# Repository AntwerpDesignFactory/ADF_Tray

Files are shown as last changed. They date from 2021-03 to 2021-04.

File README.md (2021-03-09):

# Vaccine preparation tray

## The problem
The fight against the Covid-19 pandemic continues and countries are setting up vaccination strategies to protect their population. Many hospitals and vaccination centres worldwide are dealing with challenges of setting-up a fast, efficient, and safe vaccination plan.  

One of the challenges is the preparation of the vaccine syringes. Covid-19 vaccines are delivered in vials containing 6 to 11 doses, depending on the producer of the vaccine. Doses from the vial need to be drawn up into syringes, so that one syringe can be used to vaccinate one patient. 

To speed up the vaccination process, preparation of the vaccine syringes is done by the pharmacy and injection of the vaccine is done by a nurse or physician. This means that the vaccine syringes need to be transported from the pharmacy to the location where the vaccine is administered. It is also necessary to keep track of which vaccine (producer and lot number) every patient receives. That is why correct labelling of transported vaccines is particularly important.  

At the moment, hospitals and vaccination centres often use so-called ‘kidney dish’ to collect and transport syringes. Kidney dishes are used for various medical applications; however, this bowl is not always the best solution. Syringes are mixed up which makes it difficult to take out one, because of this, precious time is lost, and it can lead to administering errors. Healthcare organisations were looking for a better alternative to transport the vaccine syringes. 

## The design
IMAGE ALT TEXT (https://www.youtube.com/watch?v=rdpCua8XM-c "ADF - Vaccin tray design")

- It fits all syringes we so far have seen selected for COVID-19 vaccine applications. Ranging from 6 to 11 mm diameter and volumes of 1 to 2 ml.
- The Tray is designed to hold the syringes of one vial of Moderna vaccine (11 doses), one vial AstraZeneca vaccine (8 to 10 doses) and two vials of Pfizer vaccine (two times 6 doses).
- Trays are securely stackable, both filled with syringes and empty. Empty trays nest into each other, this way saving space. 
- The general dimensions of the tray are roughly an A4 in size and 2 cm tall. This size should fit most actively used fridges or trolleys conveniently. 
- On both sides is a flat surface foreseen to place a label of the specific vial brand, batch and details.
- The central surface of the tray can be used to place branding in the form of a logo or a sticker.

## The benefits
- Syringes nicely organized.
- Safe transportation.
- Easy to count and keep track of.
- Traceability from vial to patient.
- Quick check of volumes in each syringe.
- Re-usable by cleaning it with IPA or dish-washing it with soap.
- Securely stackable.
- Easy to take out syringes at the patients side. 
- Prevents from a accidently pushing in any plungers 

## Material choice:
### For the mould:
- We advise using high-temperature, high density polyurethane tooling foam for this application 
- Organizations with experience can use their materials of choice for the mould.
- MDF might also be suitable, but might break after a few uses since the design contains thin-high pieces. 
- 3D printing may also be a good choice. But SLA printer are preferred over FDM prints since the layer steps on FDM make the trays hard to clean.

### For the tray:
- PETG or Vivak is advised as a medical choice and provided a decent amount of stiffness. It can be vacuum formed well and can stand cleaning with IPA and soaps. 
    - A thickness of 1mm is advised to have a decent strength.
    - In PETG there are not many colour options. So clear PETG is the best option.
- PP would be the second best pick because of again its medical purpose. But is a lot harder to form well whilst vacuum forming. The material needs to be at the exact optimal temperature and often warps if not done perfect. 

## How to make it
The tray is designed to be vacuum formed out of 1mm PETG or PP. This means a mould must be made first to form the plastic sheet over.

1. The mould is milled out of a solid piece of this foam using a CNC mill.
1. The mould needs extra ventilation holes to allow air to be pulled out of the cavities. This is done with thin long drills of around a millimeter in diameter. In our mould we drilled about 50 holes in corners and deep parts.

1. The mould also needs lubrication to allow the plastic sheet to release with ease. We applied a thin coat of Vaseline, but silicone release sprays would work as well. This release agent does need to be cleaned off of the tray after forming before use.
1. In the design branding in the form of a 3D logo is left out since these small features might be hard to mill. Thus these can be added at this moment as thin 3D printed pieces.
Also two arrows are placed at this moment to help visualising what label fits with that side of the trays syringes in case the vial holds 6 doses or less.
1. Remove the protective foils from both sides of your plastic sheet.
1. Depending on your machine you first place the mould or place the sheet of plastic. But in general words prepare the machine and pre-heat the sheet of plastic.
1. As the sheet hits around 150°C (after about 30sec) it should be ready to be pulled over the mould. 
1. Let it cool down on the mould until the plastic has hardened again.
1. Take out of the machine and pull out the mould from the tray. Blowing in compressed air from the sides may help with the pop.
1. The tray is now left with a brim that can be cut off using a sharp blade, a bandsaw, a grinder of any other tool that you prefer. The cutting edge is foreseen as a flat rim that can be cut easily on the table.
1. Remove sharp edges with a file or sanding paper.
1. Clean the tray before use to remove the release agent and dust.

Check out more detailed guides online if more help is needed. For example this guide from [Formech](https://mhubchicago.com/media/148882/business/3625/PDI_Vacuum_forming_guide.pdf) is a good resource.

## Attribution
This tray is a design of the [Antwerp Design Factory](https://antwerpdesignfactory.be). 
A research group of the [department of product development](https://www.uantwerpen.be/nl/studeren/aanbod/alle-opleidingen/productontwikkeling-studeren/) at the [University of Antwerp](https://www.uantwerpen.be/nl/studeren/aanbod/alle-opleidingen/productontwikkeling-studeren/).

The design is released under a [Creative Commons Attribution Share Alike 4.0 International licence](LICENCE). So you are free to share and modify this design. May even use it for commercial use. But, are not allowed to patent the design and are required to attribute our work when sharing.

---

Shield: [][cc-by-sa]

This work is licensed under a
[Creative Commons Attribution-ShareAlike 4.0 International License][cc-by-sa].

[][cc-by-sa]

[cc-by-sa]: http://creativecommons.org/licenses/by-sa/4.0/
[cc-by-sa-image]: https://licensebuttons.net/l/by-sa/4.0/88x31.png
[cc-by-sa-shield]: https://img.shields.io/badge/License-CC%20BY--SA%204.0-lightgrey.svg

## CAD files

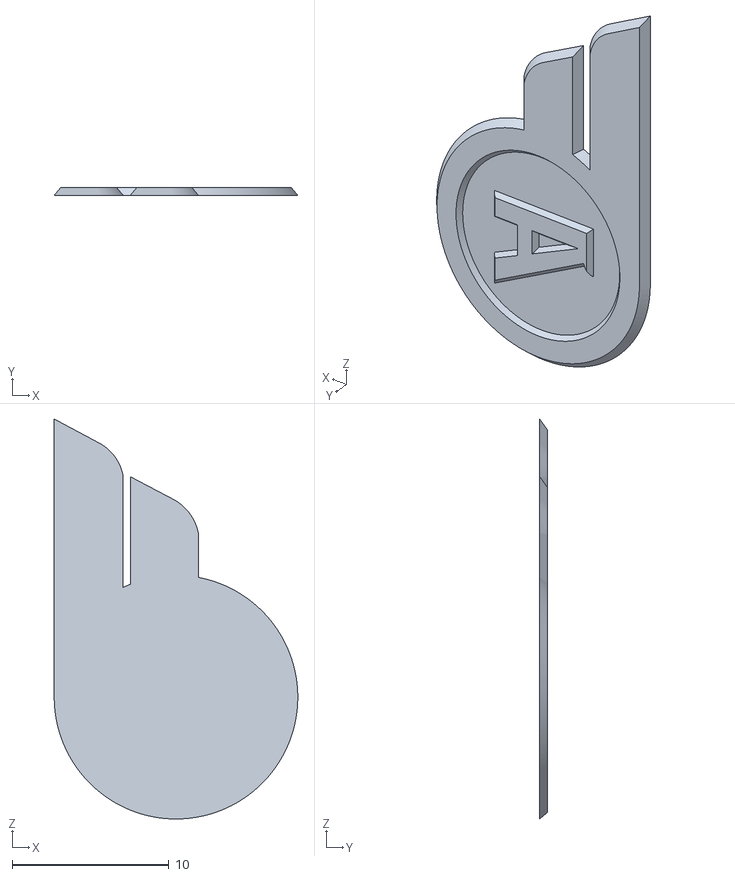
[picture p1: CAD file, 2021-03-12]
Big_tray/ADF_vaccinetray_mould - Logo.stl
15.6 x 0.49 x 25.5

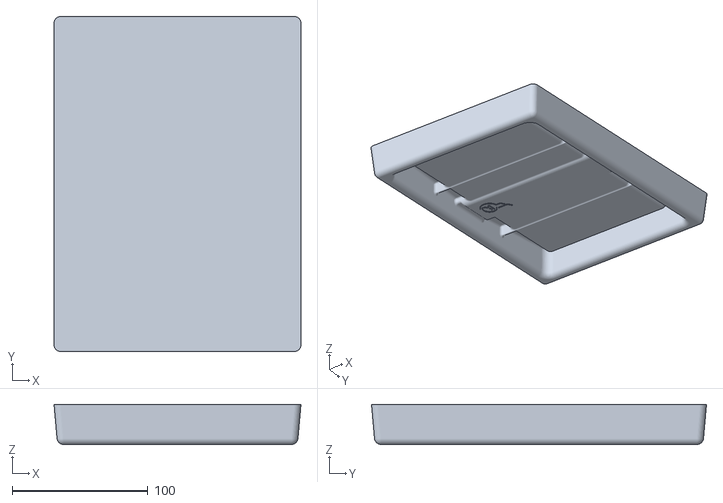
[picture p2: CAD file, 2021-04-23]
Small_tray/ADF_vaccinetray_lid_mould_small.STL
181.9 x 246.7 x 29.5

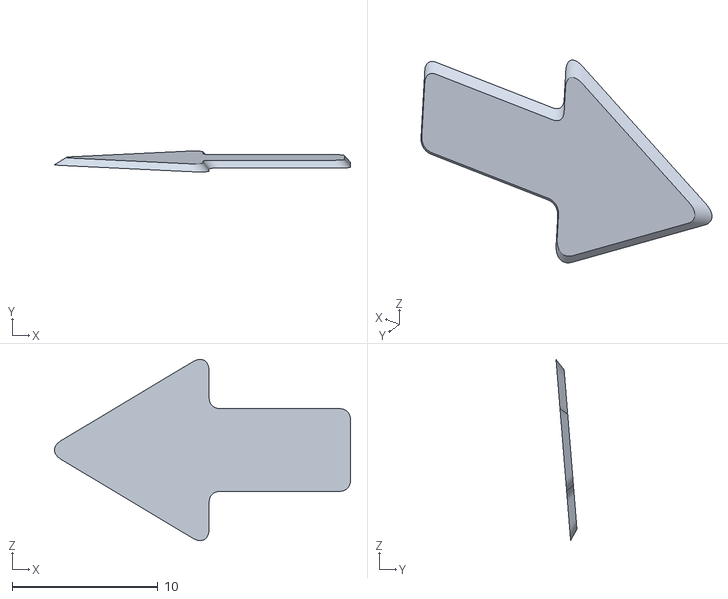
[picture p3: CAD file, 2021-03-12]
Big_tray/ADF_vaccinetray_mould - Arrows.stl
20.3 x 1.44 x 12.4

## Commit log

2021-03-10 Flipped over the mould and added the tray sample stl
2021-04-23 Added the small trays
    [ADF_vaccinetray_lid_mould_small.STL, ADF_vaccinetray_mould - Arrows.stl, ADF_vaccinetray_mould - Logo.stl]

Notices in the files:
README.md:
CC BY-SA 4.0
